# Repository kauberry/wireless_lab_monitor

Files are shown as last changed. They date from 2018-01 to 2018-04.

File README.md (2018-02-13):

## Wireless Lab Monitor ##
A simple MySensors-based, network-connected telemetry device for monitoring status of equipment in a biological laboratory setting.

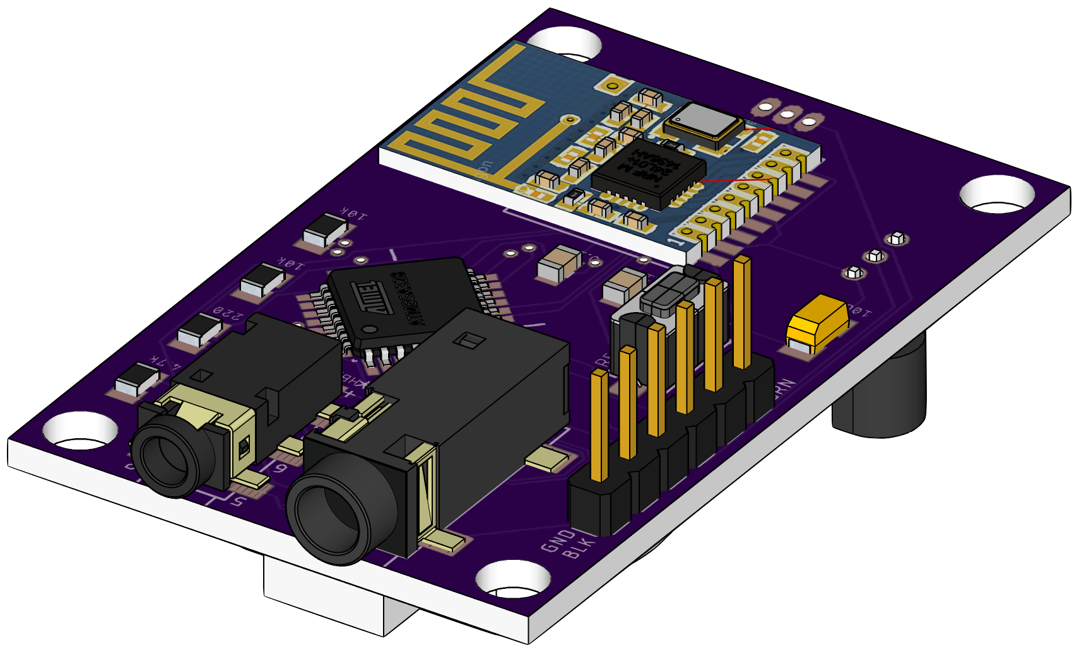
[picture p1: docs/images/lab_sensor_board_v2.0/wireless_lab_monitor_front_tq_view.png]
Populated Board Top View
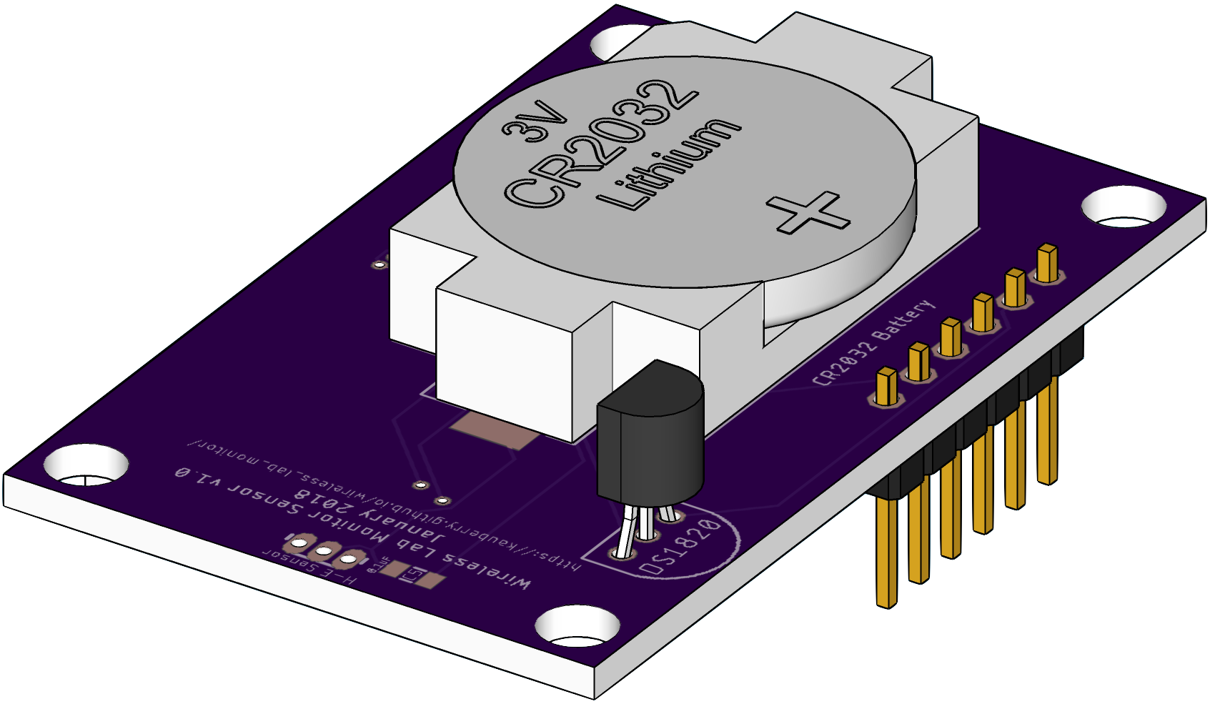
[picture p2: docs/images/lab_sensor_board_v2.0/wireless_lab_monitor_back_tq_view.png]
Populated Board Bottom View


### Rationale ###
Biological experiments are important. Biological experiments are sensitive to changes in temperature, humidity, and lots of other things. Let's use a bit of IoT technology for good instead of evil, shall we?

This initial prototype sensor will look after things like incubators and autoclaves to take note of the status of their doors and temperatures in an effort to keep their contents safe and viable.

### System Design ###
The sensors will communicate through a [MySensors](https://www.mysensors.org)-based gateway running on a [Raspberry Pi Model 3](https://www.raspberrypi.org/products/raspberry-pi-3-model-b/). This gateway box then sends the gathered telemetry data to a server via the [MQTT](http://mqtt.org) protocol where it is stored in a local database and presented through a web interface and a corresponding RESTful API.

### Hardware Description - Single Item Sensor ###
The prototype uses a standard surface mount [Microchip/Atmel ATmega328p](https://www.microchip.com/wwwproducts/en/ATMEGA328P) in a TQFP32 package, coupled with a [Nordic Semiconductor nRF24L01 Tranceiver](https://www.nordicsemi.com/eng/Products/2.4GHz-RF/nRF24L01P) to communicate with the aforementional backend server. Sensor hardware includes temperature sensors ([Dallas/Maxim DS18b20 Digital Thermometer](https://www.maximintegrated.com/en/products/analog/sensors-and-sensor-interface/DS18B20.html)) along with Hall-effect-based position sensors ([Allegro A1104](https://www.allegromicro.com/en/Products/Magnetic-Digital-Position-Sensor-ICs/Hall-Effect-Unipolar-Switches/A1101-2-3-4-6.aspx) or similar) for door open/closed status detection. Jacks are provided to add external versions of the same sensors if placement is an issue.

#### Parts Manifest ####

|Quantity | Value         |        Name        |        Package|
|-------: | ------------- | :----------------: | -------------:|
|       1 | ATMEGA328P-AU |   Microprocessor   |           TQFP|
|       2 | 10uF          |    Tantalum Cap    |           1206|
|       4 | 0.1uF         |     Capacitor      |           0805|
|       1 | green         |        LED         |           0603|
|       3 | 10kΩ          |      Resistor      |           0805|
|       1 | 4.7kΩ         |      Resistor      |           0805|
|       1 | 220Ω          |      Resistor      |           0805|
|       1 | CR2032        |   Battery Holder   ||
|       1 | 2.5mm         |     Audio Jack     |         PJ-242|
|       1 | 3.5mm         |     Audio Jack     |         PJ-328|
|       1 |               |     SMT Switch     ||
|       1 |               | Temperature Sensor |        DS18B20|
|       1 |               | Hall-Effect Sensor |          A3144|
|       1 | 1x6           |     Pin Header     | FTDI Interface|
|       1 | NRF24         |       Radio        |       Mini SMT|

#### Layout ####
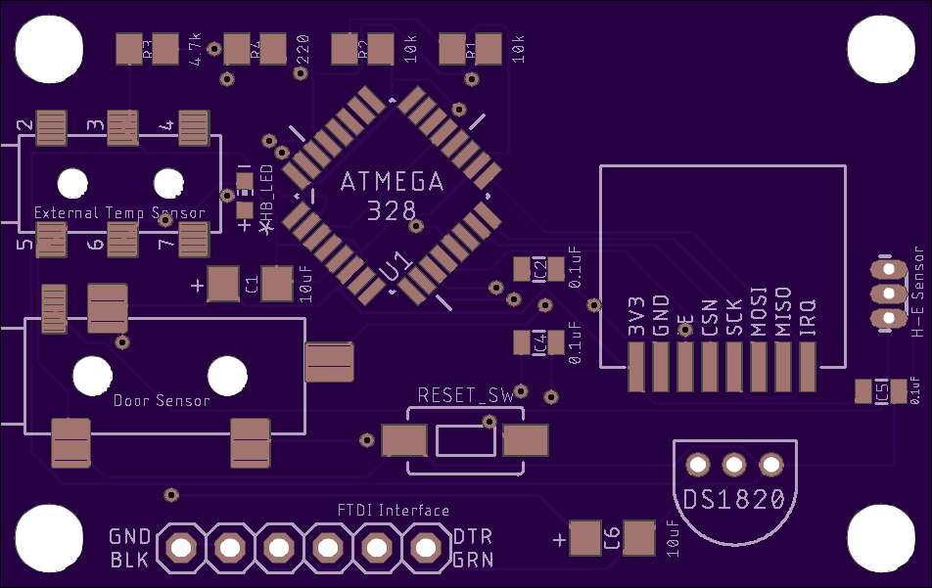
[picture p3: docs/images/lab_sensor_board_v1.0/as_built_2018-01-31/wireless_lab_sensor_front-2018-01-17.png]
Single Sensor Board Front
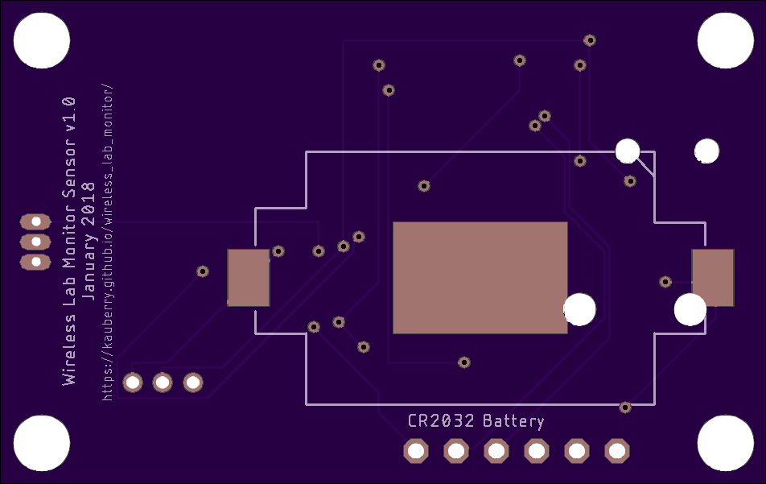
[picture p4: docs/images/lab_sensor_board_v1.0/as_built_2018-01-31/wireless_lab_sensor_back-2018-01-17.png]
Single Sensor Board Back


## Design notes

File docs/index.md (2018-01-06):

## Wireless Lab Monitor
This is just a test page for this project while I figure things out.

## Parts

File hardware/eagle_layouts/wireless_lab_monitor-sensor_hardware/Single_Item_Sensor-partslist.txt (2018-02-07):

(2) 10uF  Tantalum Cap  1206
(4) 0.1uF Capacitor 0805
(1) green LED 0603
(3) 10kΩ  Resistor  0805
(1) 4kΩ Resistor  0805
(1) 220Ω  Resistor  0805
(1) CR2032  Battery Holder
(1) 2.5mm Audio Jack  PJ-242
(1) 3.5mm Audio Jack  PJ-328
(1) SMT Switch
(1)   Temperature Sensor  DS18B20
(1)   Hall-Effect Sensor  A3144
(1)   ATMEGA328P-AU TQFP
(1) 1x6 Pin Header  FTDI Interface
(1) NRF24 Mini SMT Radio

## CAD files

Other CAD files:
docs/sketchup_files/1x6 Pin Header.skp

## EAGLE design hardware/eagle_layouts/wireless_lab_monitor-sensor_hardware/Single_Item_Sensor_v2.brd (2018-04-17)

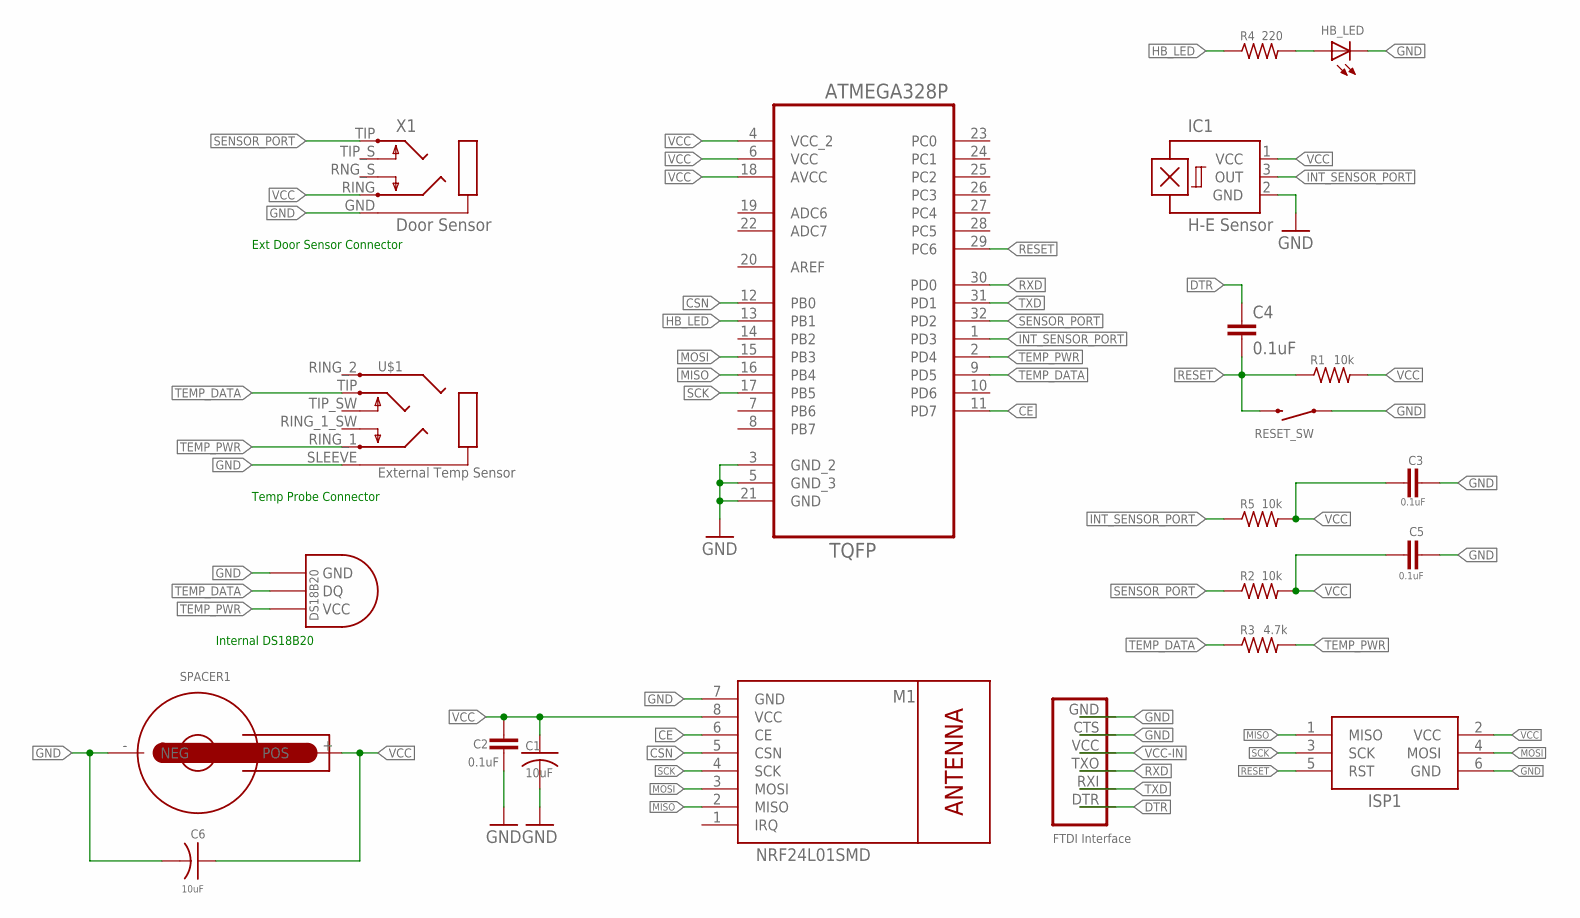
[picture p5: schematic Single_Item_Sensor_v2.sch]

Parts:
C1, C6: 10uF; C1206
C2, C3, C4, C5: 0.1uF; 0805
HB_LED: LEDCHIP-LED0603; CHIP-LED0603
IC1: H-E Sensor; SIP3-UA
ISP1: AVRISP-6; AVRISP
M1: NRF24L01SMD; WIRELESS-NRF24L01-SMD
R1, R2, R5: 10k; M0805
R3: 4.7k; M0805
R4: 220; M0805
RESET_SW: Reset; TACTILE-SWITCH-1101NE
SPACER1: WA-BCPH_SMT_79527141; 79527141
U1: ATMEGA328P-AU; QFP80P900X900X120-32N
U$1: External Temp Sensor; PJ-242
U$2: DS1820TO92; DS1820
U$3: FTDI Interface; 1X6-FTDI
X1: Door Sensor; PG203J

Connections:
CE: M1.6 (CE), U1.11 (PD7)
CSN: M1.5 (CSN), U1.12 (PB0)
DTR: C4.1, U$3.DTR
GND: C1.2, C2.2, C3.2, C5.2, C6.2, HB_LED.C, IC1.2 (GND), ISP1.6 (GND), M1.7 (GND), RESET_SW.P$1 (1), SPACER1.- (NEG), U1.3 (GND_2), U1.5 (GND_3), U1.21 (GND), U$1.SLEEVE (5), U$2.GND, U$3.CTS, U$3.GND, X1.GND (1)
HB_LED: R4.1, U1.13 (PB1)
INT_SENSOR_PORT: IC1.3 (OUT), R5.1, U1.1 (PD3)
LED+: HB_LED.A, R4.2
MISO: ISP1.1 (MISO), U1.16 (PB4)
MOSI: ISP1.4 (MOSI), U1.15 (PB3)
RESET: C4.2, ISP1.5 (RST), R1.1, RESET_SW.P$2 (2), U1.29 (PC6)
RXD: U1.30 (PD0), U$3.TXO
SCK: ISP1.3 (SCK), U1.17 (PB5)
SENSOR_PORT: R2.1, U1.32 (PD2), X1.TIP (5)
TEMP_DATA: R3.1, U1.9 (PD5), U$1.TIP (6), U$2.DQ
TEMP_PWR: R3.2, U1.2 (PD4), U$1.RING_1 (3), U$2.VDD (VCC)
TXD: U1.31 (PD1), U$3.RXI
VCC: C1.1, C2.1, C3.1, C5.1, C6.1, IC1.1 (VCC), ISP1.2 (VCC), M1.8 (VCC), R1.2, R2.2, R5.2, SPACER1.+ (POS), U1.4 (VCC_2), U1.6 (VCC), U1.18 (AVCC), X1.RING (2)
VCC-IN: U$3.VCC

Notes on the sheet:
Internal DS18B20
Temp Probe Connector
Ext Door Sensor Connector

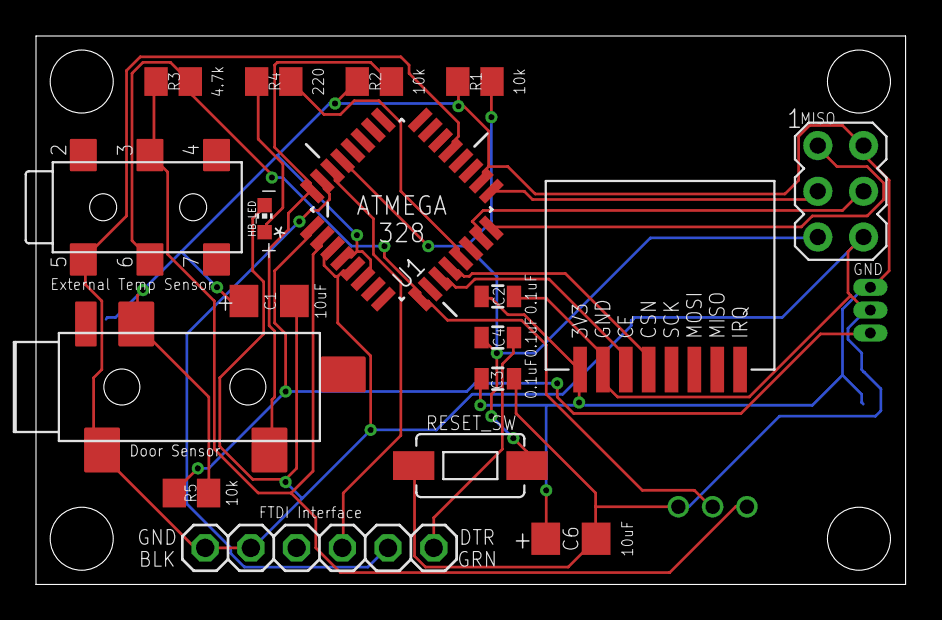
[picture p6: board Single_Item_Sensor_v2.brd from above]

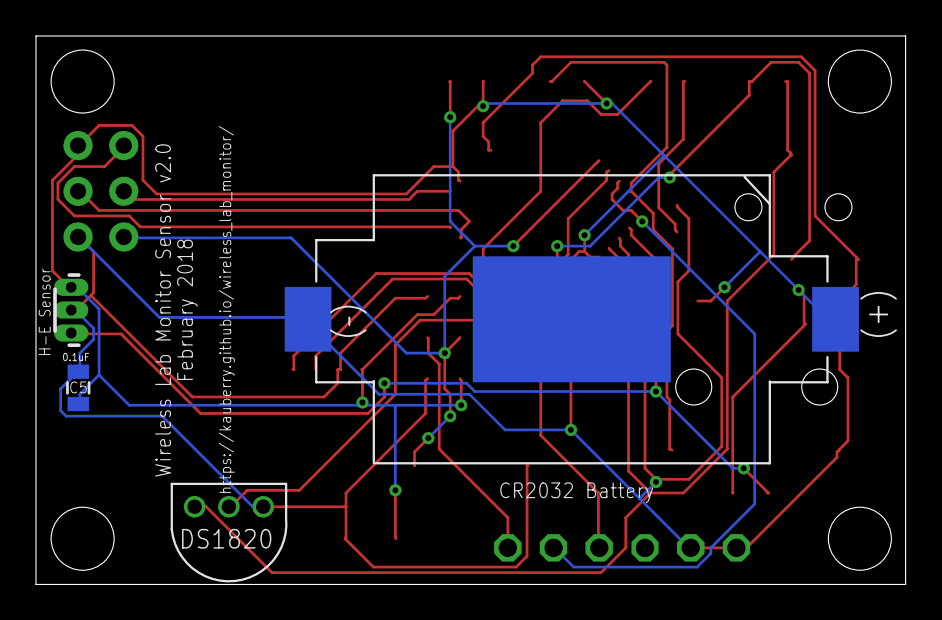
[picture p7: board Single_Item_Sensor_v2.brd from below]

Board: 2 copper layers, 48.3 x 30.5 mm, 22 parts (4 on the bottom side), 17 nets.

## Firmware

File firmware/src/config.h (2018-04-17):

#ifndef config_h
#define config_h

/**********************************
 * Sketch configuration
 */

#define SKETCH_NAME "NodeManager"
#define SKETCH_VERSION "1.0"

/**********************************
 * MySensors node configuration
 */

// General settings
#define MY_BAUD_RATE 9600
#define MY_DEBUG
// #define MY_NODE_ID 100
//#define MY_SMART_SLEEP_WAIT_DURATION_MS 500
#define MY_SPLASH_SCREEN_DISABLED
// #define MY_SIGNAL_REPORT_ENABLED
// NRF24 radio settings
#define MY_RADIO_NRF24
#define MY_RF24_CS_PIN 10
#define MY_RF24_CE_PIN 9
//#define MY_RF24_ENABLE_ENCRYPTION
//#define MY_RF24_CHANNEL 76
//#define MY_RF24_PA_LEVEL RF24_PA_HIGH
// #define MY_DEBUG_VERBOSE_RF24
//#define MY_RF24_DATARATE RF24_250KBPS

// Message signing settings
//#define MY_SIGNING_SOFT
//#define MY_SIGNING_SOFT_RANDOMSEED_PIN 7
//#define MY_SIGNING_REQUEST_SIGNATURES
//#define MY_SIGNING_ATSHA204

// OTA Firmware update settings
//#define MY_OTA_FIRMWARE_FEATURE
//#define OTA_WAIT_PERIOD 300
//#define FIRMWARE_MAX_REQUESTS 2
//#define MY_OTA_RETRY 2

/***********************************
 * NodeManager configuration
 */

// if enabled, enable debug messages on serial port
#define DEBUG 1

// if enabled, enable the capability to power on sensors with the arduino's pins to save battery while sleeping
#define POWER_MANAGER 1
// if enabled, will load the battery manager library to allow the battery level to be reported automatically or on demand
#define BATTERY_MANAGER 1
// if enabled, allow modifying the configuration remotely by interacting with the configuration child id
#define REMOTE_CONFIGURATION 0
// if enabled, persist the remote configuration settings on EEPROM
#define PERSIST 1
// if enabled, a battery sensor will be created at BATTERY_CHILD_ID (201 by default) and will report vcc voltage together with the battery level percentage
#define BATTERY_SENSOR 1
// if enabled, a signal sensor will be created at RSSI_CHILD_ID (202 by default) and will report the signal quality of the transport layer
#define SIGNAL_SENSOR 0
// if enabled, send a SLEEPING and AWAKE service messages just before entering and just after leaving a sleep cycle and STARTED when starting/rebooting
#define SERVICE_MESSAGES 0

// Enable this module to use one of the following sensors: SENSOR_ANALOG_INPUT, SENSOR_LDR, SENSOR_THERMISTOR, SENSOR_ML8511, SENSOR_ACS712, SENSOR_RAIN, SENSOR_SOIL_MOISTURE
#define MODULE_ANALOG_INPUT 0
// Enable this module to use one of the following sensors: SENSOR_DIGITAL_INPUT
#define MODULE_DIGITAL_INPUT 1
// Enable this module to use one of the following sensors: SENSOR_DIGITAL_OUTPUT, SENSOR_RELAY, SENSOR_LATCHING_RELAY
#define MODULE_DIGITAL_OUTPUT 0
// Enable this module to use one of the following sensors: SENSOR_DHT11, SENSOR_DHT22
#define MODULE_DHT 0
// Enable this module to use one of the following sensors: SENSOR_SHT21, SENSOR_HTU21D
#define MODULE_SHT21 0
// Enable this module to use one of the following sensors: SENSOR_SWITCH, SENSOR_DOOR, SENSOR_MOTION
#define MODULE_SWITCH 1
// Enable this module to use one of the following sensors: SENSOR_DS18B20
#define MODULE_DS18B20 1
// Enable this module to use one of the following sensors: SENSOR_BH1750
#define MODULE_BH1750 0
// Enable this module to use one of the following sensors: SENSOR_MLX90614
#define MODULE_MLX90614 0
// Enable this module to use one of the following sensors: SENSOR_BME280
#define MODULE_BME280 0
// Enable this module to use one of the following sensors: SENSOR_SONOFF
#define MODULE_SONOFF 0
// Enable this module to use one of the following sensors: SENSOR_BMP085
#define MODULE_BMP085 0
// Enable this module to use one of the following sensors: SENSOR_HCSR04
#define MODULE_HCSR04 0
// Enable this module to use one of the following sensors: SENSOR_MCP9808
#define MODULE_MCP9808 0
// Enable this module to use one of the following sensors: SENSOR_MQ
#define MODULE_MQ 0
// Enable this module to use one of the following sensors: SENSOR_MHZ19
#define MODULE_MHZ19 0
// Enable this module to use one of the following sensors: SENSOR_AM2320
#define MODULE_AM2320 0
// Enable this module to use one of the following sensors: SENSOR_TSL2561
#define MODULE_TSL2561 0
// Enable this module to use one of the following sensors: SENSOR_PT100
#define MODULE_PT100 0
// Enable this module to use one of the following sensors: SENSOR_BMP280
#define MODULE_BMP280 0
// Enable this module to use one of the following sensors: SENSOR_DIMMER
#define MODULE_DIMMER 0
// Enable this module to use one of the following sensors: SENSOR_RAIN_GAUGE, SENSOR_POWER_METER, SENSOR_WATER_METER
#define MODULE_PULSE_METER 0

#endif

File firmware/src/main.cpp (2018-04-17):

#include <Arduino.h>
/*
   NodeManager is intended to take care on your behalf of all those common tasks a MySensors node has to accomplish, speeding up the development cycle of your projects.
   NodeManager includes the following main components:
   - Sleep manager: allows managing automatically the complexity behind battery-powered sensors spending most of their time sleeping
   - Power manager: allows powering on your sensors only while the node is awake
   - Battery manager: provides common functionalities to read and report the battery level
   - Remote configuration: allows configuring remotely the node without the need to have physical access to it
   - Built-in personalities: for the most common sensors, provide embedded code so to allow their configuration with a single line
   Documentation available on: https://github.com/mysensors/NodeManager
 */


// load user settings
#include "config.h"
// include supporting libraries
#ifdef MY_GATEWAY_ESP8266
  #include <ESP8266WiFi.h>
#endif
// load MySensors library
//
#include <MySensors.h>
// load NodeManager library
#include "NodeManager.h"

// create a NodeManager instance
NodeManager nodeManager;

// before
void before() {
  // setup the serial port baud rate
  Serial.begin(MY_BAUD_RATE);

  /*
   * Register below your sensors
   */
  nodeManager.setBatteryMin(1.9);
  nodeManager.setBatteryMax(3.0);
  nodeManager.setSleepHours(1);
  nodeManager.setBatteryReportHours(1);
  nodeManager.setBatteryReportWithInterrupt(true);
  nodeManager.setBatteryInternalVcc(true);
  nodeManager.setSleepInterruptPin(true);
  nodeManager.setPowerPins(-1, 4, 1000);
  nodeManager.setAutoPowerPins(false);
  // nodeManager.setADCOff();

  int int_door = nodeManager.registerSensor(SENSOR_DOOR, 3, 1);
  // int ext_door = nodeManager.registerSensor(SENSOR_DOOR, 2, 2);
  int int_temp = nodeManager.registerSensor(SENSOR_DS18B20, 5, 5);
  // int ext_temp = nodeManager.registerSensor(SENSOR_DS18B20, 5, 6);

  const char* door_sensor_int_name = "Onboard Door Sensor";
  // const char* door_sensor_ext_name = "External Door Sensor";
  const char* temp_sensor_int_name = "Onboard Temp Sensor";
  // const char* temp_sensor_ext_name = "External Temp Sensor";

  SensorDoor* door_sensor_int = ((SensorDoor*) nodeManager.getSensor(int_door));
  door_sensor_int->setInterrupt(3, CHANGE, 0);
  door_sensor_int->setReportIntervalMinutes(60);
  door_sensor_int->setDescription((char*) door_sensor_int_name);
  // door_sensor_int->setPin(LOW);

  // SensorDoor* door_sensor_ext = (SensorDoor*) nodeManager.getSensor(ext_door);
  // door_sensor_ext->setInterrupt(2, CHANGE, 0);
  // door_sensor_ext->setReportIntervalMinutes(60);
  // door_sensor_ext->setDescription((char*) door_sensor_ext_name);

  wait(1000);
  SensorDs18b20* temp_sensor_int = (SensorDs18b20*) nodeManager.getSensor(int_temp);
  temp_sensor_int->setReportIntervalMinutes(60);
  temp_sensor_int->setDescription((char*) temp_sensor_int_name);

  // SensorDs18b20* temp_sensor_ext = (SensorDs18b20*) nodeManager.getSensor(ext_temp);
  // temp_sensor_ext->setReportIntervalMinutes(60);
  // temp_sensor_ext->setDescription((char*) temp_sensor_ext_name);


  /*
   * Register above your sensors
   */
  nodeManager.before();
}

// presentation
void presentation() {
  // call NodeManager presentation routine
  nodeManager.presentation();
}

// setup
void setup() {
  // call NodeManager setup routine
  nodeManager.setup();
  pinMode(3, INPUT);
  digitalWrite(3, LOW);
}

// loop
void loop() {
  // call NodeManager loop routine
  nodeManager.loop();
  delay(100);
}

// receive
void receive(const MyMessage &message) {
  // call NodeManager receive routine
  nodeManager.receive(message);
}

// receiveTime
void receiveTime(unsigned long ts) {
// call NodeManager receiveTime routine
  nodeManager.receiveTime(ts);
}

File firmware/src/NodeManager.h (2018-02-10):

/*
 * NodeManager
 */
#ifndef NodeManager_h
#define NodeManager_h

#include <Arduino.h>

// define NodeManager version
#define VERSION "1.6"

/***********************************
   Constants
*/

// define board status
#define AWAKE 0
#define SLEEP 1

// define time unit
#define SECONDS 0
#define MINUTES 1
#define HOURS 2
#define DAYS 3

// define on/off
#define OFF 0
#define ON 1

// define value type
#define TYPE_INTEGER 0
#define TYPE_FLOAT 1
#define TYPE_STRING 2
#define TYPE_DOUBLE 2

// define interrupt pins
#define INTERRUPT_PIN_1 3
#define INTERRUPT_PIN_2 2

// define eeprom addresses
#define EEPROM_SLEEP_SAVED 0
#define EEPROM_SLEEP_1 5
#define EEPROM_SLEEP_2 6
#define EEPROM_SLEEP_3 7
#define EEPROM_USER_START 100

// define requests

/************************************
 * Include user defined configuration settings
 */

#include "config.h"

/***********************************
   Default configuration settings
*/
// if enabled, enable debug messages on serial port
#ifndef DEBUG
  #define DEBUG 1
#endif

// if enabled, enable the capability to power on sensors with the arduino's pins to save battery while sleeping
#ifndef POWER_MANAGER
  #define POWER_MANAGER 1
#endif
// if enabled, will load the battery manager library to allow the battery level to be reported automatically or on demand
#ifndef BATTERY_MANAGER
  #define BATTERY_MANAGER 1
#endif
// if enabled, allow modifying the configuration remotely by interacting with the configuration child id
#ifndef REMOTE_CONFIGURATION
  #define REMOTE_CONFIGURATION 1
#endif
// if enabled, persist the configuration settings on EEPROM
#ifndef PERSIST
  #define PERSIST 0
#endif

// if enabled, send a SLEEPING and AWAKE service messages just before entering and just after leaving a sleep cycle
#ifndef SERVICE_MESSAGES
  #define SERVICE_MESSAGES 0
#endif
// if enabled, a battery sensor will be created at BATTERY_CHILD_ID (201 by default) and will report vcc voltage together with the battery level percentage
#ifndef BATTERY_SENSOR
  #define BATTERY_SENSOR 1
#endif
// if enabled, a RSSI sensor will be created at SIGNAL_CHILD_ID (202 by default) and will report the signal quality of the transport layer
#ifndef SIGNAL_SENSOR
  #define SIGNAL_SENSOR 1
#endif

// the child id used to allow remote configuration
#ifndef CONFIGURATION_CHILD_ID
  #define CONFIGURATION_CHILD_ID 200
#endif
// the child id used to report the battery voltage to the controller
#ifndef BATTERY_CHILD_ID
  #define BATTERY_CHILD_ID 201
#endif
// the child id used to report the rssi level to the controller
#ifndef SIGNAL_CHILD_ID
  #define SIGNAL_CHILD_ID 202
#endif
// define the maximum number of sensors that can be managed
#ifndef MAX_SENSORS
  #define MAX_SENSORS 10
#endif
// define default sketch name and version
#ifndef SKETCH_NAME
  #define SKETCH_NAME "NodeManager"
#endif
#ifndef SKETCH_VERSION
  #define SKETCH_VERSION "1.0"
#endif


/***********************************
   Default module settings
*/

// Enable this module to use one of the following sensors: SENSOR_ANALOG_INPUT, SENSOR_LDR, SENSOR_THERMISTOR, SENSOR_ML8511, SENSOR_ACS712, SENSOR_RAIN, SENSOR_SOIL_MOISTURE
#ifndef MODULE_ANALOG_INPUT
  #define MODULE_ANALOG_INPUT 0
#endif
// Enable this module to use one of the following sensors: SENSOR_DIGITAL_INPUT
#ifndef MODULE_DIGITAL_INPUT
  #define MODULE_DIGITAL_INPUT 0
#endif
// Enable this module to use one of the following sensors: SENSOR_DIGITAL_OUTPUT, SENSOR_RELAY, SENSOR_LATCHING_RELAY
#ifndef MODULE_DIGITAL_OUTPUT
  #define MODULE_DIGITAL_OUTPUT 0
#endif
// Enable this module to use one of the following sensors: SENSOR_DHT11, SENSOR_DHT22
#ifndef MODULE_DHT
  #define MODULE_DHT 0
#endif
// Enable this module to use one of the following sensors: SENSOR_SHT21, SENSOR_HTU21D
#ifndef MODULE_SHT21
  #define MODULE_SHT21 0
#endif
// Enable this module to use one of the following sensors: SENSOR_SWITCH, SENSOR_DOOR, SENSOR_MOTION
#ifndef MODULE_SWITCH
  #define MODULE_SWITCH 0
#endif
// Enable this module to use one of the following sensors: SENSOR_DS18B20
#ifndef MODULE_DS18B20
  #define MODULE_DS18B20 0
#endif
// Enable this module to use one of the following sensors: SENSOR_BH1750
#ifndef MODULE_BH1750
  #define MODULE_BH1750 0
#endif
// Enable this module to use one of the following sensors: SENSOR_MLX90614
#ifndef MODULE_MLX90614
  #define MODULE_MLX90614 0
#endif
// Enable this module to use one of the following sensors: SENSOR_BME280
#ifndef MODULE_BME280
  #define MODULE_BME280 0
#endif
// Enable this module to use one of the following sensors: SENSOR_SONOFF
#ifndef MODULE_SONOFF
  #define MODULE_SONOFF 0
#endif
// Enable this module to use one of the following sensors: SENSOR_BMP085
#ifndef MODULE_BMP085
  #define MODULE_BMP085 0
#endif
// Enable this module to use one of the following sensors: SENSOR_HCSR04
#ifndef MODULE_HCSR04
  #define MODULE_HCSR04 0
#endif
// Enable this module to use one of the following sensors: SENSOR_MCP9808
#ifndef MODULE_MCP9808
  #define MODULE_MCP9808 0
#endif
// Enable this module to use one of the following sensors: SENSOR_MQ
#ifndef MODULE_MQ
  #define MODULE_MQ 0
#endif
// Enable this module to use one of the following sensors: SENSOR_MHZ19
#ifndef MODULE_MHZ19
  #define MODULE_MHZ19 0
#endif
// Enable this module to use one of the following sensors: SENSOR_AM2320
#ifndef MODULE_AM2320
  #define MODULE_AM2320 0
#endif
// Enable this module to use one of the following sensors: SENSOR_TSL2561
#ifndef MODULE_TSL2561
  #define MODULE_TSL2561 0
#endif
// Enable this module to use one of the following sensors: SENSOR_PT100
#ifndef MODULE_PT100
  #define SENSOR_PT100 0
#endif
// Enable this module to use one of the following sensors: SENSOR_BMP280
#ifndef MODULE_BMP280
  #define MODULE_BMP280 0
#endif
// Enable this module to use one of the following sensors: SENSOR_DIMMER
#ifndef MODULE_DIMMER
  #define MODULE_DIMMER 0
#endif
// Enable this module to use one of the following sensors: SENSOR_RAIN_GAUGE, SENSOR_POWER_METER, SENSOR_WATER_METER
#ifndef MODULE_PULSE_METER
  #define MODULE_PULSE_METER 0
#endif
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

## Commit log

2018-01-06 Initial hardware commit
    [Single_Item_Sensor.brd, Single_Item_Sensor.sch]
2018-02-07 Moving things around for better consistency
    [1x6 Pin Header.skp, Single_Item_Sensor.brd, Single_Item_Sensor.sch, Single_Item_Sensor_v2.brd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]
2018-02-07 Initial commit of single item sensor firmware code
2018-02-10 Adding v2 hardware designs
    [Single_Item_Sensor_v2.brd, Single_Item_Sensor_v2.sch]
2018-02-10 Updating board specification files
2018-04-17 Working version with NodeManager 1.6
    [Single_Item_Sensor_v2.brd, Single_Item_Sensor_v2.sch]

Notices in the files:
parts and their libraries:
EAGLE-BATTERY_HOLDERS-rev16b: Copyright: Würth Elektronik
